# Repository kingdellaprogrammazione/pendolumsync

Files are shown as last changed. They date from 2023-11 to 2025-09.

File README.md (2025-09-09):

# Sincronizzazione di due pendoli accoppiati

In questa repository è presente il materiale prodotto per l'esame di Sistemi Complessi della triennale in fisica di Bologna. L'oggetto dello studio è il fenomeno di sincronizzazione tra due pendoli accoppiati tramite un'asta.
Di seguito è presentato un breve riassunto del lavoro effettuato; una descrizone completa è presente nel report.

## Analisi meccanica del moto di due pendoli accoppiati

<p align="center">
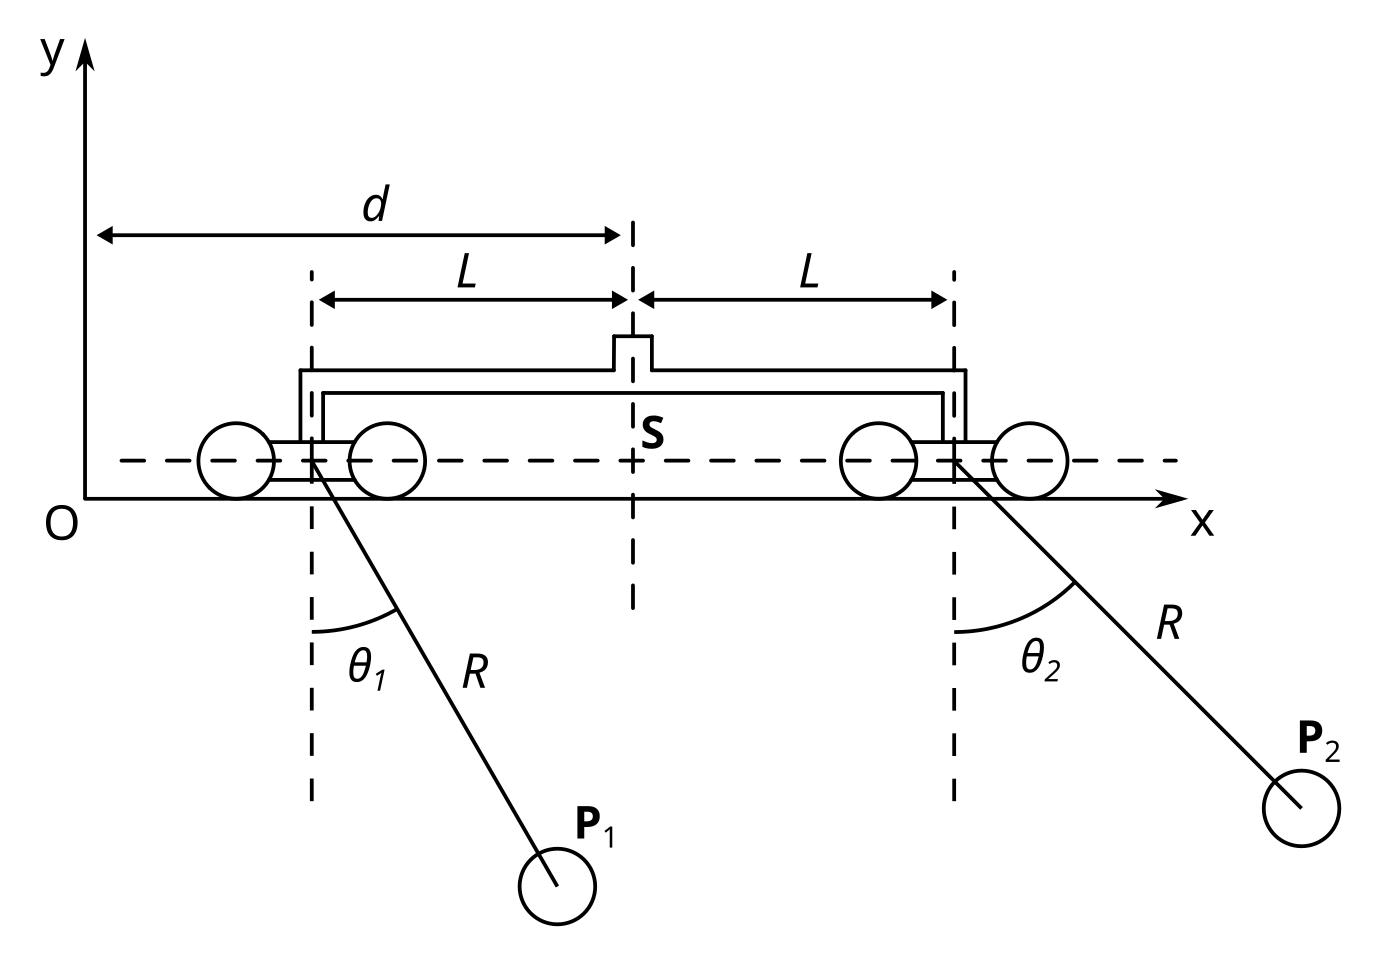
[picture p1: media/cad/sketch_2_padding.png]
  
</p>

Senza considerare attriti, dalla figura si calcola la lagrangiana del sistema, a meno di costanti, come

$$
\mathcal{L}_{PO} =  \left(m+ \frac{M}{2}\right) \dot{d}^2 + \frac{m R^2}{2}  (\dot\theta_1^2 + \dot\theta_2^2) + m \dot{d} R (\dot \theta_1 + \dot \theta_2) - \frac{m gR}{2} (\theta_1^2 + \theta_2^2) .
$$

## Equazioni del moto in assenza di attrito

Per proseguire è necessario approssimare la lagrangiana nel regime di piccole oscillazioni e sfruttare un cambio di coordinate per gli angoli: 

$$\begin{array}{c}
h = \theta_1 + \theta_2 , \\
q = \theta_1 - \theta_2.
\end{array}
$$

E' possibile utilizzare ora un'altra funzione, la funzione di Routh, per poter eliminare un grado di libertà. Si ottiene immediatamente

$$  \mathcal{R}_{PO} = \frac{1}{2} \frac{(p_d -mR\dot h)^2}{2m + M}- \frac{mR^2}{4}  (\dot{h}^2 + \dot{q}^2) + \frac{mgR}{4}(h^2 + q^2) . $$ 

Si può così completamente ricostruire il moto del sistema. Si nota che, partendo da una situazione iniziale arbitraria, la condizione di sincronizzazione in fase equivale alla richiesta che $q$ tenda a zero, mentre quella in controfase equivale alla richiesta che $h$ tenda a zero. Occorre fare attenzione al fatto
che però nella soluzione dell'equazione il moto evidentemente non può convergere, essendo hamiltoniano, ad una soluzione particolare, fatta eccezione per alcune condizioni iniziali patologiche.

## Equazioni del moto in presenza di attrito

Affinchè il moto converga ad una soluzione particolare, come accade nella realtà, è necessario tenere conto dei fenomeni dissipativi. Potrebbe ad esempio essere considerato l'attrito che si sviluppa nel perno dei pendoli, quello generato dal movimento delle ruote dei carrelli, sia radente che volvente, e quello tra l'aria e le varie componenti mobili. Si supponga di voler includere nelle equazioni del moto un termine proporzionale alle velocità angolari , con costante comune di proporzionalità gamma, avente le dimensioni di una frequenza. Riscrivendo le equazioni del moto e aggiugnendo alle forze generalizzate l'attrito citato sopra si ottengono due equazioni

$$  R \ddot \theta_i + \ddot d = - g \theta_i  - \gamma   \dot \theta_i, \qquad i =1,2 .
$$

Dopo qualche sostituzione, sfruttando la coordinata ciclica d si possono riscrivere le due equazioni con le nuove variabili.  La considerazione decisiva per osservare il fenomeno della sincronizzazione consiste nel considerare la costante gamma diversa per i due modi di oscillazione; differenziando le nuove costanti
con un pedice, si tiene conto di effetti dissipativi che influenzano in modo differente il modo di oscillazione in fase rispetto a quello in controfase.  È evidente quindi che se le costanti gamma sono diverse, l'ampiezza di uno di questi due modi va a zero più velocemente rispetto all'altro, sincronizzando il moto. In conclusione le equazioni considerate sono:

$$  
\begin{split}
  \ddot h + \gamma_h \dot h + \omega_h^2 h  = 0, \\
  \ddot q +\gamma_h \dot q + \omega_q^2 q = 0 .
  \end{split}
$$

# Apparato sperimentale

## Materiale utilizzato

Riferirsi al report.

## Realizzazione pratica del modello

Inizialmente la realizzazione del progetto era stata pensata tramite una rotaia a cuscino d'aria, per poter studiare il fenomeno, nella sua parte transiente, per un periodo di tempo lungo, grazie al poco attrito; questa idea però è stata abbandonata dopo alcuni tentativi per le numerose difficoltà sperimentali. Successivamente si è provato ad usare delle costruzioni giocattolo per la creazione di una rotaia e carrellini; purtroppo anche questo tentativo è stato accantonato a causa di notevoli imperfezioni e mancanza di allineamento tra i vari pezzi di rotaia.

In seguito si è pensato quindi di utilizzare un'altro tipo di rotaia di laboratorio, dotata di carrellini con ruote. La progettazione del modello si è rivolta, una volta recuperata l'apparecchiatura di laboratorio, alla costruzione dei supporti, disegnati tramite un software di modellizzazione tridimensionale e stampati con una stampante 3D. 

<p align="center">
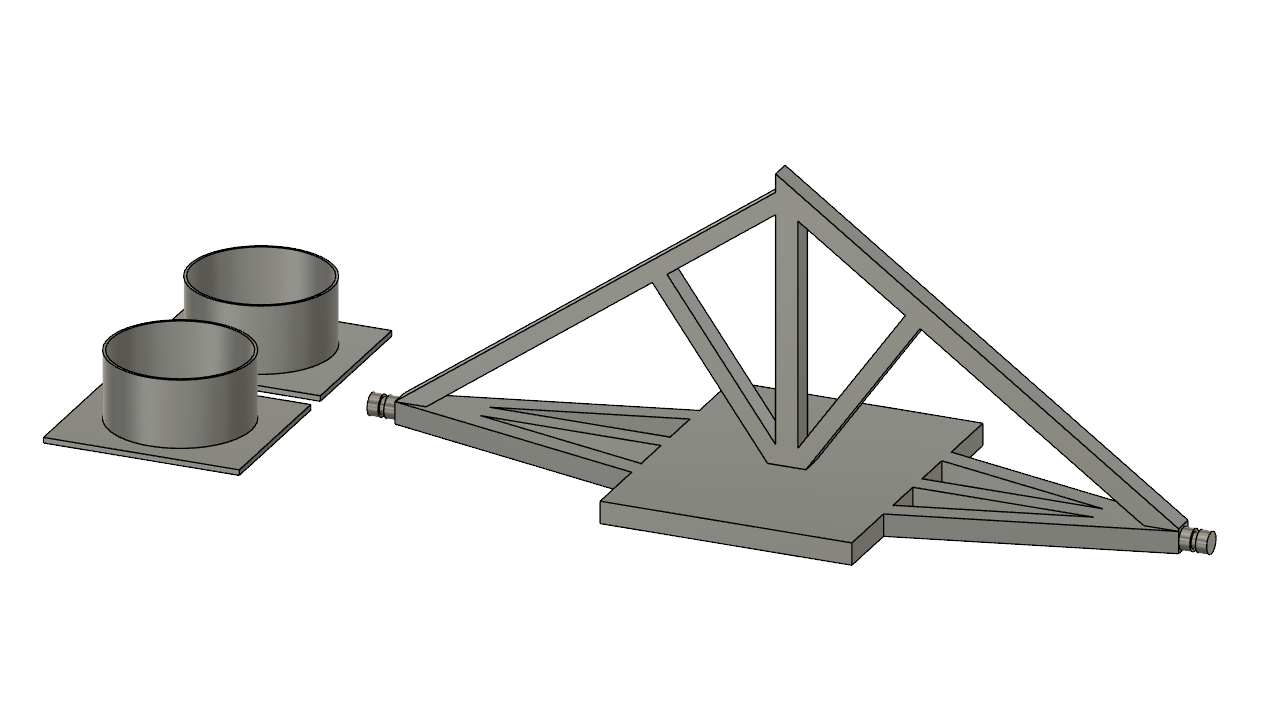
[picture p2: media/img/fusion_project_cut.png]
  
</p>

L'apparato sperimentale completo è mostrato nella figura seguente:

<p align="center">
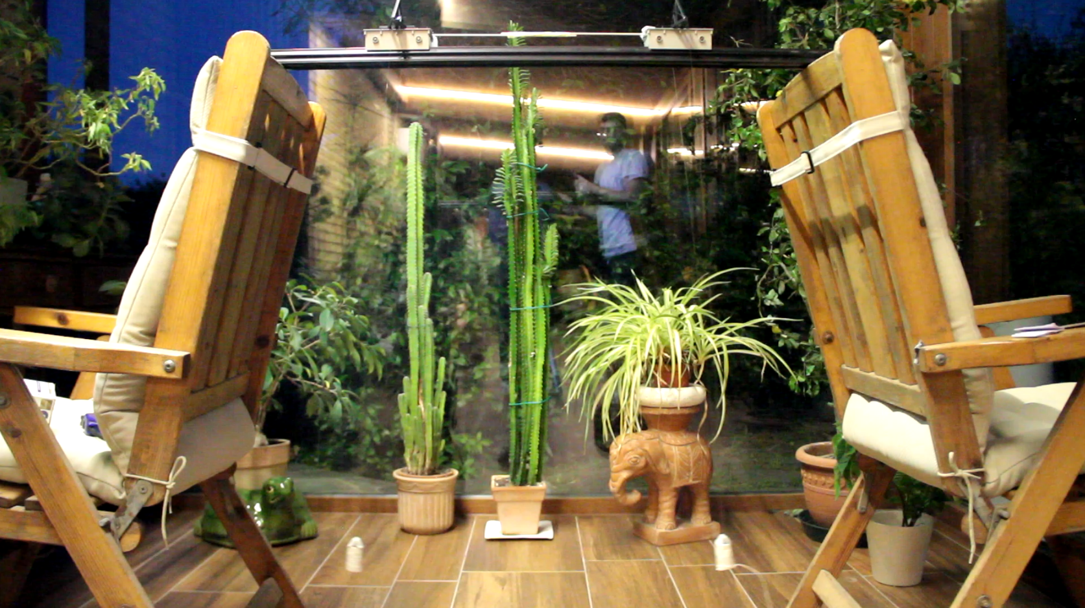
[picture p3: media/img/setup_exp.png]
  
</p>

## Esecuzione dell'esperimento

Una volta sistemati tutti gli elementi, sono stati acquisiti differenti video del fenomeno, avendo la cura di avere una condizione iniziale statica, con i tutti gli elementi fermi rispetto al sistema di riferimento della stanza. Questa ipotesi è stata  realizzata inizialmente collegando, dopo aver fermato il pendolo di sinistra, con un lungo spago fatto circolare attorno all'apparato, il pendolo e il carrello di destra. In questo modo si puntava ad eliminare l'errore dato dalla non coincidenza degli istanti di rilascio dei due elementi, che sarebbero invece stati messi in moto nello stesso momento al taglio dello spago. Questo sistema, però, è risultato inadatto in quanto lo spago, una volta tagliato, continuava a disturbare il movimento dell'apparecchio introducendo un nuovo attrito e distorcendo il fenomeno. Si è provato quindi ad agire nel modo più semplice: fermando il pendolo di sinistra, trattenendo con una mano il carrellino di destra e con l'altra lo spago collegato al rispettivo pendolo. 

## Scrittura dei programmi per l'acquisizione e l'elaborazione dati

Per quanto riguarda la scrittura dei programmi, si è scelto di utilizzare la libreria [OpenCV](https://opencv.org/), una libreria open source utilizzabile in particolare nel linguaggio di programmazione C++, destinata all'analisi di immagini e video. In questo esperimento la libreria è stata utilizzata nel per tracciare il movimento nel tempo dei pendoli e dei carrellini, in maniera automatizzata. E' stato utilizzato il C++ per la nota velocità in esecuzione rispetto a python. 

# Risultati e discussione

Il grafico degli angoli al trascorrere del tempo è mostrato nella figura seguente.

<p align="center">
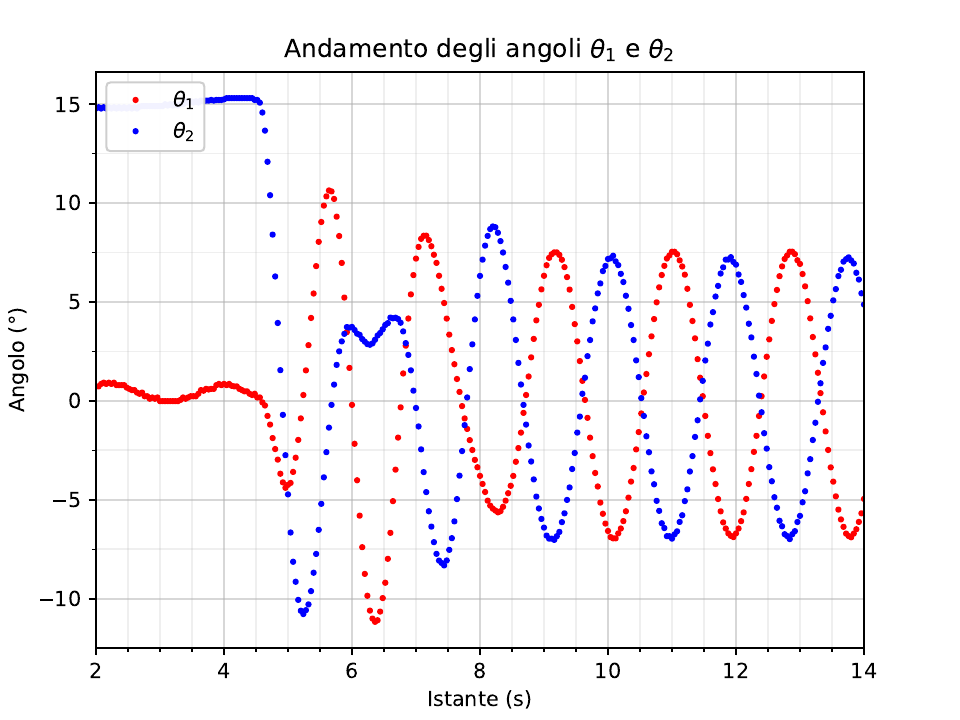
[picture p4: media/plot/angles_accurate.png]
  
</p>

Si nota come, dopo un breve periodo iniziale di quiete, in cui il pendolo 1 si trova in quiete, mentre il pendolo 2 descrive piccole oscillazioni dell'ampiezza di circa 1°, che si è cercato di ridurre il più possibile manualmente, il sistema viene lasciato libero di evolvere. Dopo un momento di transizione, in cui i pendoli e i carrellini descrivono il loro complicato moto, circa dall'istante 4.6 all'istante 8.5, il sistema mantiene il suo moto nella condizione di oscillazioni in controfase, quindi con i carrellini necessariamente fermi, per la conservazione della quantità di moto iniziale, nulla.

Possono quindi essere costruite e analizzate le variabili h e q mostrate al variare del tempo:

<p align="center">
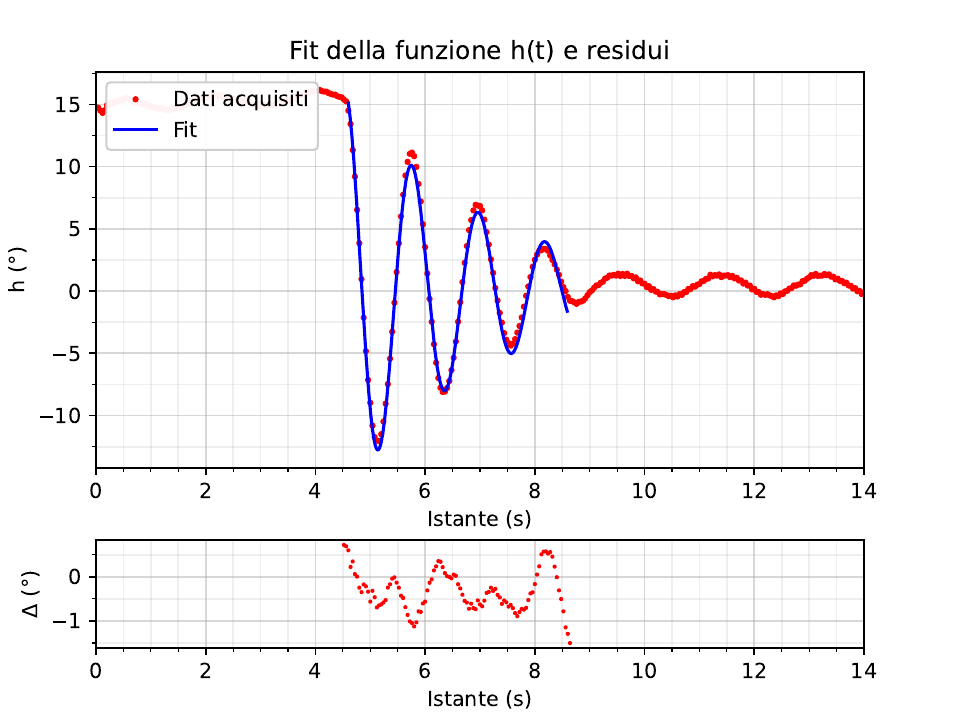
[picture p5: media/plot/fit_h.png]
  
</p>

<p align="center">
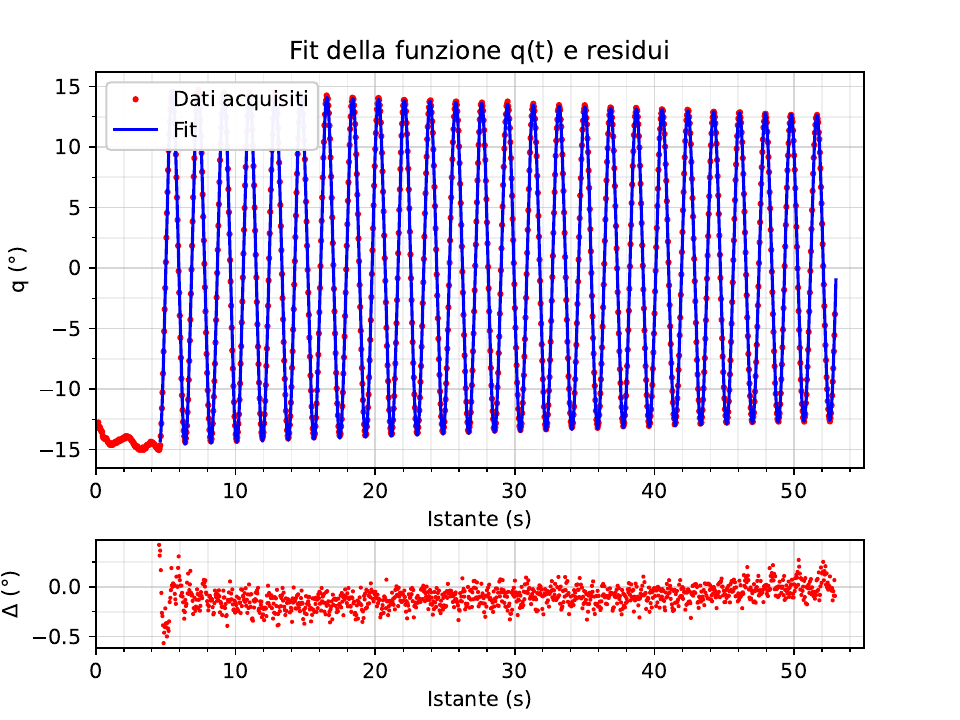
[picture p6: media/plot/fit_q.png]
  
</p>

In queste due figure sono anche presenti i due fit delle equazioni teoriche che dovrebbero regolare il moto delle due variabili; in basso sono mostrati anche i residui, ossia la differenza, calcolata punto per punto, tra i valori del fit e quelli dei punti acquisiti.

# Conclusioni

In conclusione, è stata osservata con successo la sincronizzazione di due pendoli, ossia la diminuzione dell'ampiezza a zero di un modo normale di oscillazione del sistema, fatto dovuto a differenti tassi di dissipazione di energia nei due modi appena citati. I due coefficienti $\gamma$ sono stati stimati essere pari rispettivamente a 0.77 ± 0.02 Hz per il modo in fase e 0.00631 ± 0.00006 Hz per quello in controfase.
Notiamo infine che la stima dei coefficienti di attrito data dal fit è in accordo con l'idea intuitiva legata alla caratteristica del modo di oscillazione in cui il carrello è fermo, ossia alla minor dissipazione di energia rispetto a quello in cui il carrello oscilla in opposizione di fase rispetto ai pendoli; ciò è dovuto soprattutto al maggiore attrito generato durante lo scorrimento sulla rotaia che si somma al normale attrito generato sul perno dalle oscillazioni dei pendoli. Questa sorgente di attrito è circa di 2 ordini di grandezza superiore rispetto all'altra.

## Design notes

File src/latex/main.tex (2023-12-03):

\documentclass[11pt, a4paper, twoside, italian]{article}

\usepackage{blindtext}
\usepackage{geometry}
\usepackage{setspace}
\usepackage{titlesec}
\usepackage{indentfirst}
\usepackage{graphicx}
\usepackage{babel}
\usepackage{multicol}
\usepackage{amsmath}
\usepackage{subcaption}
\usepackage[hang, flushmargin, multiple, bottom]{footmisc}
\usepackage{float}
\usepackage{array}
\usepackage{booktabs}
\usepackage{url}
\usepackage{csvsimple}
\usepackage{colortbl}
\usepackage{multicol}
\usepackage{enumerate}
\usepackage{multirow}
\usepackage{booktabs}
\usepackage{siunitx}
\usepackage{subcaption}
\usepackage[margin=0.2cm]{caption}
\usepackage{longtable}
\usepackage{physics}
\usepackage{comment}
\usepackage{listings}
\usepackage{xcolor}
\usepackage{enumitem}
\usepackage{wrapfig}
\usepackage{hyperref}
\usepackage{cleveref}
\usepackage[ddmmyyyy]{datetime}
\usepackage[export]{adjustbox}
% for watermark
%\usepackage{draftwatermark}
%\SetWatermarkText{\includegraphics{../../media/img/draft_watermark.png}}

\titlespacing*{\section}{0px}{3mm}{1mm}
\titlespacing*{\subsection}{0px}{3mm}{1mm}
\geometry{
  left=2cm,
  right=2cm,
  top=2cm,
  bottom=2cm
}
\setlength{\parindent}{10mm}

\author{Edoardo Frulla}
\date{Corso "Introduzione ai sistemi complessi" \\ \vspace{0.3cm} I semestre a.a. 2022/2023 \\ \vspace{0.3cm} \today}
\title{Sincronizzazione di due pendoli accoppiati}  

\definecolor{codegreen}{rgb}{0,0.6,0}
\definecolor{codegray}{rgb}{0.5,0.5,0.5}
\definecolor{codepurple}{rgb}{0.58,0,0.82}
\definecolor{backcolour}{rgb}{0.95,0.95,0.92}
  
\lstdefinestyle{mystyle}{
  backgroundcolor=\color{backcolour},   
  commentstyle=\color{codegreen},
  keywordstyle=\color{magenta},
  numberstyle=\tiny\color{codegray},
  stringstyle=\color{codepurple},
  basicstyle=\ttfamily\footnotesize,
  breakatwhitespace=false,         
  breaklines=true,                 
  captionpos=b,                    
  keepspaces=true,                 
  numbers=left,                    
  numbersep=5pt,                  
  showspaces=false,                
  showstringspaces=false,
  showtabs=false,               
  tabsize=2,
  inputencoding = utf8,  % Input encoding
  extendedchars = true,  % Extended ASCII
  literate      =        % Support additional characters
    {á}{{\'a}}1  {é}{{\'e}}1  {í}{{\'i}}1 {ó}{{\'o}}1  {ú}{{\'u}}1
    {Á}{{\'A}}1  {É}{{\'E}}1  {Í}{{\'I}}1 {Ó}{{\'O}}1  {Ú}{{\'U}}1
    {à}{{\`a}}1  {è}{{\`e}}1  {ì}{{\`i}}1 {ò}{{\`o}}1  {ù}{{\`u}}1
    {À}{{\`A}}1  {È}{{\`E}}1  {Ì}{{\`I}}1 {Ò}{{\`O}}1  {Ù}{{\`U}}1
    {ä}{{\"a}}1  {ë}{{\"e}}1  {ï}{{\"i}}1 {ö}{{\"o}}1  {ü}{{\"u}}1
    {Ä}{{\"A}}1  {Ë}{{\"E}}1  {Ï}{{\"I}}1 {Ö}{{\"O}}1  {Ü}{{\"U}}1
    {â}{{\^a}}1  {ê}{{\^e}}1  {î}{{\^i}}1 {ô}{{\^o}}1  {û}{{\^u}}1
    {Â}{{\^A}}1  {Ê}{{\^E}}1  {Î}{{\^I}}1 {Ô}{{\^O}}1  {Û}{{\^U}}1
    {œ}{{\oe}}1  {Œ}{{\OE}}1  {æ}{{\ae}}1 {Æ}{{\AE}}1  {ß}{{\ss}}1
    {ẞ}{{\SS}}1  {ç}{{\c{c}}}1 {Ç}{{\c{C}}}1 {ø}{{\o}}1  {Ø}{{\O}}1
    {å}{{\aa}}1  {Å}{{\AA}}1  {ã}{{\~a}}1  {õ}{{\~o}}1 {Ã}{{\~A}}1
    {Õ}{{\~O}}1  {ñ}{{\~n}}1  {Ñ}{{\~N}}1  {¿}{{?`}}1  {¡}{{!`}}1
    {°}{{\textdegree}}1 {º}{{\textordmasculine}}1 {ª}{{\textordfeminine}}1
    {£}{{\pounds}}1  {©}{{\copyright}}1  {®}{{\textregistered}}1
    {«}{{\guillemotleft}}1  {»}{{\guillemotright}}1  {Ð}{{\DH}}1  {ð}{{\dh}}1
    {Ý}{{\'Y}}1    {ý}{{\'y}}1    {Þ}{{\TH}}1    {þ}{{\th}}1    {Ă}{{\u{A}}}1
    {ă}{{\u{a}}}1  {Ą}{{\k{A}}}1  {ą}{{\k{a}}}1  {Ć}{{\'C}}1    {ć}{{\'c}}1
    {Č}{{\v{C}}}1  {č}{{\v{c}}}1  {Ď}{{\v{D}}}1  {ď}{{\v{d}}}1  {Đ}{{\DJ}}1
    {đ}{{\dj}}1    {Ė}{{\.{E}}}1  {ė}{{\.{e}}}1  {Ę}{{\k{E}}}1  {ę}{{\k{e}}}1
    {Ě}{{\v{E}}}1  {ě}{{\v{e}}}1  {Ğ}{{\u{G}}}1  {ğ}{{\u{g}}}1  {Ĩ}{{\~I}}1
    {ĩ}{{\~\i}}1   {Į}{{\k{I}}}1  {į}{{\k{i}}}1  {İ}{{\.{I}}}1  {ı}{{\i}}1
    {Ĺ}{{\'L}}1    {ĺ}{{\'l}}1    {Ľ}{{\v{L}}}1  {ľ}{{\v{l}}}1  {Ł}{{\L{}}}1
    {ł}{{\l{}}}1   {Ń}{{\'N}}1    {ń}{{\'n}}1    {Ň}{{\v{N}}}1  {ň}{{\v{n}}}1
    {Ő}{{\H{O}}}1  {ő}{{\H{o}}}1  {Ŕ}{{\'{R}}}1  {ŕ}{{\'{r}}}1  {Ř}{{\v{R}}}1
    {ř}{{\v{r}}}1  {Ś}{{\'S}}1    {ś}{{\'s}}1    {Ş}{{\c{S}}}1  {ş}{{\c{s}}}1
    {Š}{{\v{S}}}1  {š}{{\v{s}}}1  {Ť}{{\v{T}}}1  {ť}{{\v{t}}}1  {Ũ}{{\~U}}1
    {ũ}{{\~u}}1    {Ū}{{\={U}}}1  {ū}{{\={u}}}1  {Ů}{{\r{U}}}1  {ů}{{\r{u}}}1
    {Ű}{{\H{U}}}1  {ű}{{\H{u}}}1  {Ų}{{\k{U}}}1  {ų}{{\k{u}}}1  {Ź}{{\'Z}}1
    {ź}{{\'z}}1    {Ż}{{\.Z}}1    {ż}{{\.z}}1    {Ž}{{\v{Z}}}1
    % ¿ and ¡ are not correctly displayed if inconsolata font is used
    % together with the lstlisting environment. Consider typing code in
    % external files and using \lstinputlisting to display them instead.      
    % reference to this answer https://tex.stackexchange.com/questions/24528/having-problems-with-listings-and-utf-8-can-it-be-fixed
    % and https://tex.stackexchange.com/questions/105672/special-characters-in-input-file
}

\lstset{style=mystyle}

\sisetup{separate-uncertainty=true}
%per mettere il più meno

\begin{document}
\maketitle
    \begin{abstract}
        In questo documento si introduce il fenomeno emergente della sincronizzazione.
        Si sceglie poi un sistema composto da due pendoli accoppiati per analizzare le caratteristiche
        dinamiche che lo portano alla sincronizzazione, giungendo alla conlcusione che
        la causa del fenomeno sia la differenza tra i tassi di dissipazione dei principali
        modi normali di oscillazione.
        Infine si effettua un esperimento per valutare la bontà della previsione teorica.
    \end{abstract}

\section{Introduzione}
La sincronizzazione è un particolare fenomeno che si manifesta in natura in differenti modalità: ne sono esempi gli sciami di lucciole che tendono a lampeggiare all'unisono, le cellule del cuore umano che emettono impulsi elettrici in fase permettendo le contrazioni cardiache, gli applausi che si sviluppano nel pubblico durante le opere teatrali e i neuroni che emettono segnali elettrici, amplificandone gli effetti, durante gli episodi di epilessia.
In tutti questi casi sono considerate situazioni in cui i singoli elementi che causano il fenomeno, a cui è associata una grandezza caratteristica che oscilla secondo un periodo proprio generalmente arbitrario, si trovano ad interagire e influenzandosi l'un l'altro giungono in qualche modo alla sincronizzazione più o meno completa dell'insieme di cui fanno parte.
Le interazioni che abbiamo descritto fino ad ora sono però manifestazione di interazioni non fondamentali dal punto di vista fisico: si tratta di fenomeni emergenti. 
Esistono però anche delle situazioni in cui la sincronizzazione è attribuibile alle interazioni fisiche fondamentali: possiamo per esempio pensare ai sistemi meccanici composti da pendoli o metronomi accoppiati.

Un problema di questo tipo fu affrontato per la prima volta nel Febbraio 1665, dal fisico Olandese Christiaan Huygens: doveva affrontare il problema di migliorare la precisione degli orologi a pendolo, anche essi da lui inventati. Si trovava nella sua stanza a causa di una "leggera indisposizione" quando si accorse che due orologi a pendolo che aveva costruito si erano spontaneamente sincronizzati. Provò allora, sospettando un accoppiamento dovuto al mezzo con cui si trovavano entrambi in contatto, a svolgere alcuni esperimenti, in particolare agganciandone due a un supporto in legno sospeso tra due sedie, come si nota da \cref{pendoli_huygens}.
\begin{figure}
    \centering
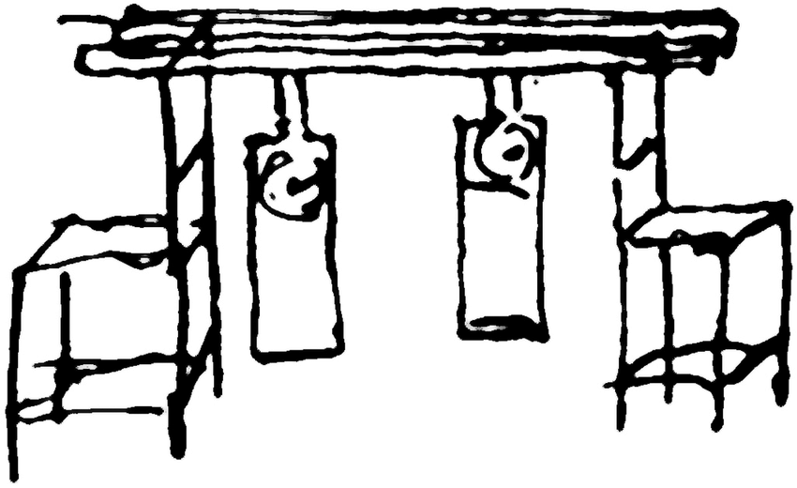
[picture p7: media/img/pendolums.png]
    
    \caption{\textit{Schema della situazione sperimentale disegnato da Huygens. I due orologi sono sospesi a un supporto comune.}}
    \label{pendoli_huygens}
\end{figure}
Un problema più semplice da affrontare rispetto a quello dei due orologi a pendolo è quello di due pendoli posti su una base comune, libera di muoversi lungo un asse.
\section{Analisi meccanica del moto di due pendoli accoppiati}
\begin{figure}[h]
    \centering
    
    \caption{\textit{Modello del sistema costruito con indicate
     le grandezze rilevanti. Le lettere maiuscole in grassetto indicano dei punti, quelle in corsivo delle 
     costanti; le minuscole invece indicano le variabili.} }
    \label{pendolicorpolibero}
\end{figure}
Innanzitutto si consideri il diagramma indicato in \cref{pendolicorpolibero}.
I tre corpi coinvolti nella dinamica sono i due pendoli, il cui centro 
geometrico è indicato dai punti $\mathbf{P}_1$ e $\mathbf{P}_2$, entrambi di massa $m$,
e il supporto rigido, costituito da due carrellini identici collegati tra loro da un'asta,
indicato dal punto $\mathbf{S}$, arbitrariamente fissato lungo l'asse di simmetria del sistema 
parallelo all'asse $y$, di massa $M$. In questo caso, per comodità il punto $\mathbf{S}$ 
viene fissato lungo l'asse nel punto di intersezione con l'asse di simmetria dei carrellini
parallelo all'asse $x$.

Si assuma che il sistema sia libero di muoversi esclusivamente in un piano fissato, in questo caso
il piano $xy$, e che il moto del supporto sia ristretto alla direzione $x$ (è "appoggiato" sull'asse $x$).
Si supponga che le masse dell'asta e dei fili colleganti i carrellini tra loro
e con le masse oscillanti $\mathbf{P}$ siano trascurabili rispetto alle restanti; 
inoltre si trascurino anche le masse delle ruote dei carrellini, che, se presenti, si assume ruotino senza strisciare.
Per quanto riguarda le masse dei pendoli puntiformi, queste sono pensate fissate nel centro geometrico degli stessi.
In questo modo è possibile ottenere una notevole semplificazione della trattazione analitica,
descrivendo comunque con una buona approssimazione il moto degli elementi principali.

È possibile quindi ricavare le coordinate dei tre elementi rilevanti, ossia i due pendoli e il supporto:
\begin{gather*}
\mathbf{P}_1 = (d - L + R \sin \theta_1, S_y - R \cos \theta_1 ) \, , \\
\mathbf{P}_2 = (d + L + R \sin \theta_2, S_y - R \cos \theta_2 ) \, , \\
\mathbf{S} = (d , S_y) \, .
\end{gather*}
Calcolando quindi l'energia cinetica per ogni oggetto:
\begin{gather*}
K_{\mathbf{P}_1}=  \frac{m}{2} \lVert \dot{\mathbf{P}}_1 \rVert^2 =  \frac{m}{2}(\dot{d}^2 + R^2 \dot\theta_1^2+ 2\dot{d}R\cos\theta_1 \dot{\theta_1}) \, , \\
K_{\mathbf{P}_2} = \frac{m}{2} \lVert \dot{\mathbf{P}}_2 \rVert^2 =  \frac{m}{2}(\dot{d}^2 + R^2 \dot\theta_2^2+ 2\dot{d}R\cos\theta_2 \dot{\theta_2}) \, , \\
K_{\mathbf{S}} =  \frac{M}{2} \lVert \dot{\mathbf{S}} \rVert^2 = \frac{M}{2} \dot{d}^2 \, .
\end{gather*}
L'energia potenziale invece è:
\begin{gather*}
V_{\mathbf{P}_1}= mg P_{1y} = mg (S_y - R \cos \theta_1 ) \, , \\
V_{\mathbf{P}_2} = mg P_{2y} = mg (S_y - R \cos \theta_2 ) \, , \\
V_{\mathbf{S}} = mg S_{y} \, .
\end{gather*}
E quindi la lagrangiana del sistema si calcola, a meno di costanti, come
\begin{equation*}
\mathcal{L} = K_{TOT} - V_{TOT} = \left(m+ \frac{M}{2}\right) \dot{d}^2 + \frac{m R^2}{2}  (\dot\theta_1^2 + \dot\theta_2^2) + m \dot{d} R (\cos\theta_1 \dot\theta_1 + \cos \theta_2 \dot \theta_2) + mgR(\cos\theta_1 + \cos \theta_2) \, .
\end{equation*}
\subsection{Equazioni del moto in assenza di attrito}
Per proseguire è necessario approssimare
la lagrangiana nel regime di piccole oscillazioni:
\begin{equation}
\mathcal{L}_{PO} =  \left(m+ \frac{M}{2}\right) \dot{d}^2 + \frac{m R^2}{2}  (\dot\theta_1^2 + \dot\theta_2^2) + m \dot{d} R (\dot \theta_1 + \dot \theta_2) - \frac{m gR}{2} (\theta_1^2 + \theta_2^2) \, .
\label{lagrangianapo}
\end{equation}
Si nota immediatamente che nella lagrangiana è presente una coordinata ciclica, $d$; c'è
 quindi un integrale primo del moto, cioè una quantità che resta costante durante 
l'evoluzione temporale del sistema:
\begin{equation}
p_d = \frac{\partial \mathcal{L}_{PO}}{\partial \dot{d}} =(2m+M) \dot d + m R (\dot\theta_1 + \dot \theta_2) \, .
\label{ciclica}
\end{equation}
Si può sfruttare adesso un conveniente cambio di coordinate per gli angoli:
\begin{equation}
\setlength\arraycolsep{0pt}
\renewcommand\arraystretch{1.25}
\left\{
\begin{array}{c}
h = \theta_1 + \theta_2  \\
q = \theta_1 - \theta_2
\end{array}
\right.
,
\label{definizionehq}
\end{equation}
notando che
\begin{equation*}
  \theta_1^2 + \theta_2^2 = \frac{h^2 +q^2}{2} \, .
\end{equation*}
Le relazioni precedenti valgono anche tra le derivate.
Riscrivendo la lagrangiana si ottiene
\begin{equation*}
\mathcal{L}_{PO} =  \left(m+ \frac{M}{2}\right) \dot{d}^2 + \frac{mR^2}{4}  (\dot{h}^2 + \dot{q}^2) + m  R \dot{d}\dot{h} - \frac{mgR}{4}(h^2 + q^2) \, .
\end{equation*}
L'\cref{ciclica} inoltre diventa 
\begin{equation*}
  p_d = \frac{\partial \mathcal{L}_{PO}}{\partial \dot{d}} =(2m+M) \dot d + m R \dot h \, .
\end{equation*}
E' possibile utilizzare ora un'altra funzione, la funzione di Routh $\mathcal{R}_{PO}$, per poter eliminare 
un grado di libertà nelle equazioni del moto. Questa viene ricavata a partire dalla lagrangiana, introducendo solamente il
momento $p_d$:
\begin{equation*}
\mathcal{R}_{PO}(h,\dot h, q, \dot q, d, p_d )  = 
p_d \dot{d}(d, p_d, h,\dot h, q, \dot q)- \mathcal{L}_{PO}(h,\dot h, q, \dot q, d, \dot{d}(d, p_d, h,\dot h, q, \dot q)) \, ,
\end{equation*}
dove sono state esplicitate le dipendenze dalle variabili. 
In particolare si nota che nella lagrangiana bisogna scrivere $\dot d$ sfruttando l'\cref{ciclica}.
Si ottiene immediatamente 
\begin{equation*}
  \mathcal{R}_{PO} = \frac{1}{2} \frac{(p_d -mR\dot h)^2}{2m + M}- \frac{mR^2}{4}  (\dot{h}^2 + \dot{q}^2) + \frac{mgR}{4}(h^2 + q^2) \, .
\end{equation*}
Da questa equazione si possono ricavare le equazioni del moto, le più importanti sono 
\begin{equation}
  \dot p_d = 0 \, ,
  \label{conservazione}
\end{equation}
che è ovviamente coerente con la conservazione di $p_d$ notata in \cref{ciclica}, e
\begin{equation}
  \begin{split}
  \ddot h = -\frac{\alpha}{R} h \, ,\\
  \ddot q = - \frac{g}{R} q \, ,
  \end{split}
  \label{equazionifinalinondissipate}
\end{equation}
utilizzando l'\cref{conservazione} e ponendo $\alpha = \frac{(2m + M) g}{M} $.
Con queste equazioni a disposizione si può completamente ricostruire il moto del sistema.
Si nota che, partendo da una situazione iniziale arbitraria,
la condizione di sincronizzazione in fase equivale alla richiesta che $q$ tenda a zero, mentre quella in controfase
equivale alla richiesta che $h$ tenda a zero. 
Occorre fare attenzione al fatto che però nella soluzione in \cref{equazionifinalinondissipate} sia $h$ che $q$ descrivono moti oscillatori con frequenza rispettiva
$\omega_h = \sqrt{\frac{\alpha}{R} \vphantom{\frac{g}{R}}}$ e $\omega_q = \sqrt[]{\frac{g}{R}}$.
Le uniche soluzioni per cui i pendoli oscillano sincronizzati sono quelle per cui una tra $h$ o $q$ è nulla
all'inizio del moto, restando quindi nulla per tutti gli istanti successivi.
Il moto evidentemente non converge ad una soluzione particolare, attraversa invece entrambe le configurazioni di sincronizzazione 
permanendo per il resto degli istanti in una combinazione delle due soluzioni.
\label{sezionesenzaattrito}

\subsection{Equazioni del moto in presenza di attrito}
\label{sezioneattrito}
Affinchè il moto converga ad una soluzione particolare, come accade nella realtà, 
è necessario tenere conto dei fenomeni dissipativi.
Potrebbe ad esempio essere considerato l'attrito che si sviluppa nel perno 
dei pendoli, quello generato dal movimento delle ruote dei
 carrelli, sia radente che volvente, e quello tra l'aria e le varie 
 componenti mobili.
Si supponga di voler includere nelle equazioni del moto un termine 
proporzionale alle velocità angolari $\dot \theta_1$ e $\dot \theta_2$, con costante comune di 
proporzionalità $\gamma$, avente le dimensioni di una frequenza. 
Riscrivendo le equazioni del moto 
per queste due variabili, ricavandole dalla lagrangiana in \cref{lagrangianapo} e semplificando i fattori in comune
si ottiene
\begin{equation*}
    R \ddot \theta_i + \ddot d = - g  \theta_i , \qquad i =1,2 
\end{equation*}
e si nota che è possibile aggiungere al secondo membro, in cui sono scritte le 
forze generalizzate, l'attrito citato sopra, agente ovviamente in verso 
opposto alla velocità:
\begin{equation*}
  R \ddot \theta_i + \ddot d = - g \theta_i  - \gamma   \dot \theta_i, \qquad i =1,2 \, .
\end{equation*}
Sostituendo la derivata dell'\cref{ciclica}
\begin{equation*}
  (2m + M) \ddot d = -mR (\ddot \theta_1 + \ddot \theta_2) 
\end{equation*} 
nell'equazione precedente si giunge alla coppia di equazioni:
\begin{equation*}
  R \ddot \theta_i -\frac{m}{2m + M}R (\ddot \theta_1 + \ddot \theta_2) 
  = - g \theta_i  - \gamma   \dot \theta_i \, , \qquad i =1,2 \, ,
\end{equation*}
che dopo qualche passaggio algebrico si possono riscrivere con le variabili
$h$ e $q$:
\begin{equation*}
  \begin{split}
  (R- \frac{2m}{2m + M}R) \ddot h + \gamma \dot h + g h  = 0 \, , \\
  R \ddot q +\gamma \dot q + g q = 0 \, .
  \end{split}
\end{equation*}
Manipolando algebricamente questa equazione, ridefinendo la costante
$\gamma$ e utilizzando le frequenze definite in precedenza si giunge infine a
\begin{equation*}
  \begin{split}
  \ddot h + \gamma \dot h + \omega_h^2 h  = 0 \, ,\\
  \ddot q +\gamma \dot q + \omega_q^2 q = 0 \, .
  \end{split}
\end{equation*}
La considerazione decisiva per osservare il fenomeno della sincronizzazione 
consiste nel considerare la costante $\gamma$ diversa per i due modi di oscillazione;
differenziando le nuove costanti con un pedice, si tiene conto di 
effetti dissipativi che influenzano in modo differente il modo di oscillazione
in fase rispetto a quello in controfase.
Le soluzioni generali di queste equazioni sono del tipo:
\begin{align}
    h(t) &= A_h e^{- \frac{\gamma_h}{2} t} \cos(\tilde{\omega}_h t + \beta_h) \label{equazionefinaleh} \, , \\
    q(t) &= A_q e^{- \frac{\gamma_q}{2} t} \cos(\tilde{\omega}_q t + \beta_q) \label{equazionefinaleq} \, ,
\end{align}
con $A_h$, $A_q$, $\beta_h$ e $\beta_q$ costanti reali, e dove 
\begin{equation}
\tilde{\omega}_i = \sqrt{\omega_i^2 -\left( \frac{\gamma_i}{2} \right)^2} \qquad 
i = h,q 
\, .
\label{equation:omegadef}
\end{equation}
È evidente quindi che se le costanti $\gamma$ sono diverse, l'ampiezza di uno di questi due modi va a zero più velocemente rispetto 
all'altro, sincronizzando il moto.

\section{Apparato sperimentale}
\subsection{Materiale utilizzato}

Durante l'esperimento sono stati coinvolti diversi elementi, tra cui:
\begin{enumerate}
      \item rotaia e carrellini\footnote{Attrezzatura gentilmente concessa dal liceo E.Medi di Senigallia}, mostrati in \cref{photo_crane}, con basso coefficiente di attrito solitamente
      utilizzati in esperimenti relativi alla conservazione della quantità
      di moto;
      \item due alte sedie in legno;
      \item filo di nylon trasparente;
      \item due strutture identiche, mostrate in \cref{photo_crane}, progettate autonomamente e stampate in 3D;
      \item scotch di carta;
      \item monete varie;
      \item spago da cucina;
      \item supporti in legno per spiedini.
\end{enumerate}
\begin{figure}[h!]
  \centering
\begin{minipage}[t]{0.45\textwidth}
  \centering
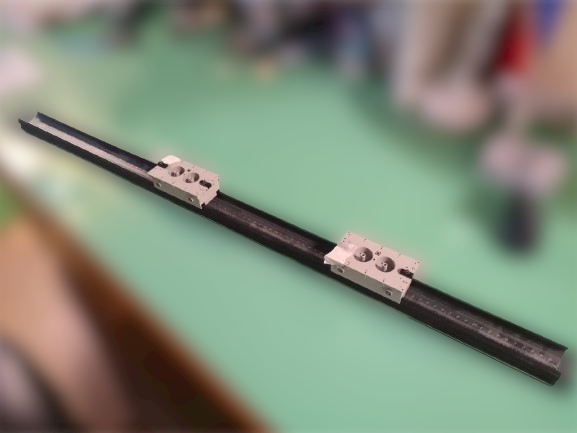
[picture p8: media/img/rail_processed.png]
  
  \caption{\textit{La rotaia e i carrellini presi in prestito.}}
  \label{photo_rail}
\end{minipage}
\begin{minipage}[t]{0.45\textwidth}
  \centering
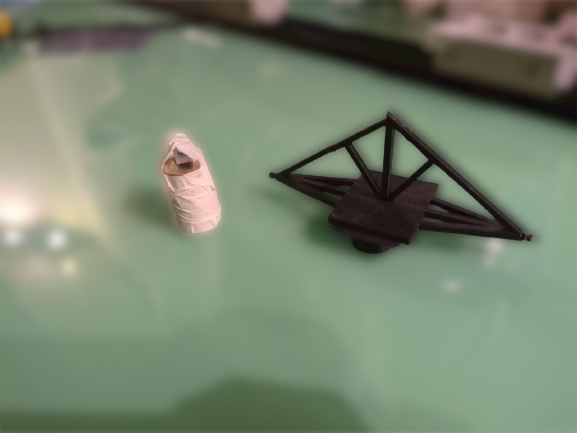
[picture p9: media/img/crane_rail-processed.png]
  
  \caption{\textit{Il pendolo (sinistra) e la struttura stampata in 3D dopo l'assemblaggio
  (destra).}}
  \label{photo_crane}
\end{minipage}
\end{figure}

\subsection{Strumenti di misura}

Per quanto riguarda gli strumenti di misura, sono stati invece utilizzati:
\begin{enumerate}
  \item bilancia da cucina (risoluzione \SI{1}{\g});
  \item macchina fotografica semi-professionale;
  \item treppiede per macchina fotografica;
  \item metro estendibile (risoluzione \SI{1}{\milli\m});
  \item livella a bolla;
  \item libreria di object tracking della suite OpenCV\footnote{https://opencv.org/}.
\end{enumerate}
\subsection{Realizzazione pratica del modello}
Inizialmente la realizzazione del progetto era stata pensata tramite 
una rotaia a cuscino d'aria, per poter studiare il fenomeno, nella sua parte transiente, 
per un periodo di tempo lungo, grazie al poco attrito; questa idea però è stata abbandonata dopo alcuni tentativi per
le numerose difficoltà sperimentali. In \cref{photo_crane_air} è mostrato uno dei modelli di supporto
progettati e stampati in 3D montabili sui carrellini della rotaia.
In seguito si è provato ad usare delle costruzioni giocattolo per la creazione di una rotaia
e carrellini; purtroppo anche questo tentativo è stato accantonato a causa di 
notevoli imperfezioni e mancanza di allineamento tra i vari pezzi di rotaia. 
Un esempio di una parte della costruzione è mostrato in \cref{photo_lego}.

\begin{figure}[h!]
  \centering
\begin{minipage}{0.45\textwidth}
  \centering
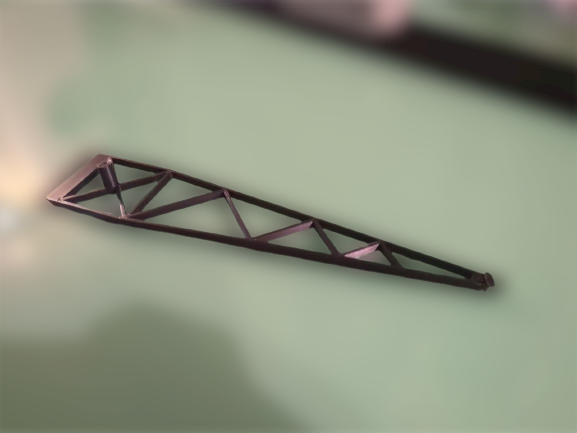
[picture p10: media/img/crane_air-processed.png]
  
  \caption{\textit{Parte della struttura relativa alla rotaia a cuscino d'aria.}}
  \label{photo_crane_air}
\end{minipage}
\begin{minipage}{0.45\textwidth}
  \centering
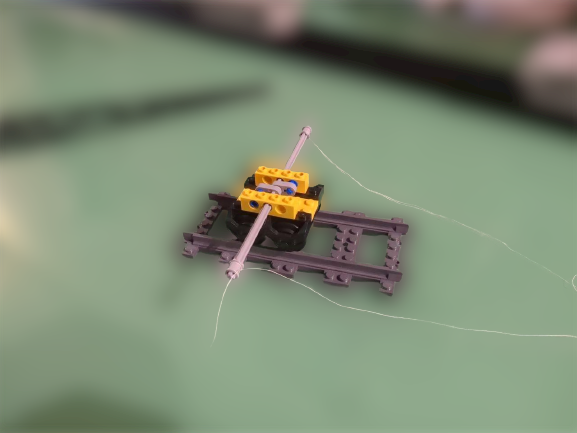
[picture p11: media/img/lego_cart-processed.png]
  
  \caption{\textit{Il modellino realizzato a partire da costruzioni giocattolo.}}
  \label{photo_lego}
\end{minipage}
\end{figure}

In seguito si è pensato quindi di utilizzare un'altro tipo di rotaia di laboratorio, dotata
di carrellini con ruote.
La progettazione del modello si è rivolta, una volta recuperata l'apparecchiatura
di laboratorio, alla costruzione dei supporti, disegnati tramite un
software di modellizzazione tridimensionale e stampati con una stampante 3D.
Una volta stampati diversi prototipi e scelto quello migliore sono state incollate
tra loro le due parti costituenti il pezzo finale indicato in \cref{photo_crane}, i cui modelli sono mostrati
in \cref{photo_piece}, e, 
incastrato il pezzo sopra ciascun carrellino, si è costruito il supporto tramite due alte sedie
sopra le quali è stata posta la rotaia. 
\begin{figure}[h!]
  \centering
  
  \caption{\textit{Le parti della struttura mostrata in \cref{photo_crane}, visualizzate nel programma
  di modellazione 3D.}}
  \label{photo_piece}
\end{figure}
È fondamentale sottolineare come si siano scelte le sedie più alte disponibili,
in quanto la lunghezza del pendolo doveva essere grande
per permettere poi l'uso dell'approssimazione di piccole oscillazioni,
non impedendo la chiara manifestazione del fenomeno della sincronizzazione.
I carrellini sono poi stati collegati tra loro tramite due bastoncini 
di legno solitamente utilizzati per la cottura degli spiedini.
La massa complessiva dei due carrellini, considerando il connettore trascurabile, è risultata essere pari a 
\SI{160 \pm 1}{\g}.
È stato controllato che lo sfondo presente dietro le
due sedie fosse inoltre fisso, ossia privo di oggetti
in movimento, per favorire il processo di tracking.
A questo punto sono stati costruiti i due pendoli identici, tramite svariate 
monete raggruppate saldamente insieme grazie all'uso dello scotch di carta, 
pesanti ciascuno \SI{139 \pm 1}{\g}.
Le monete sono state scelte per la loro elevata densità e modularità: è 
stato possibile infatti costruire diversi pendoli, di dimensioni pressochè
uguali ma di masse sensibilmente diverse gli uni dagli altri.
Sono quindi stati tagliati due pezzi approssimativamente
uguali di filo di nylon, lunghi abbastanza da sfruttare l'intera altezza 
fornita dalle due sedie, e sono poi stati agganciati ai pendoli tramite un pezzo di una nota 
marca di costruzioni giocattolo. Questi due tratti di filo sono stati poi regolati,
con l'ausilio del metro,
tramite la realizzazione di un numero adeguato di avvolgimenti nel perno di 
aggancio, fino ad ottenere una lunghezza del pendolo $R$ = \SI{85 \pm 1}{\centi\m} ciascuno (l'incertezza è 
maggiore della risoluzione del metro per tenere conto di errori nella valutazione del centro
di massa dei pendoli).
È importante notare che, per far sì che i pendoli oscillassero nello stesso piano
spaziale per tutta la durata dell'esperimento, i pendoli stessi fossero
liberi di muoversi lungo l'ansa creata dal filo di nylon appeso ai carrellini. 
A questo punto al pendolo di destra è stato collegato un breve tratto di spago 
per consentirne la manovra da una posizione che non interferisse con il tracking.
Di fronte a questa apparecchiatura, a una distanza di circa \SI{1.5}{\m}, è stato 
posizionato il treppede con sopra la macchina fotografica, per l'acquisizione
del video.
L'obiettivo della macchina fotografica è stato accuratamente posizionato, per evitare
offset prospettici in un unico verso, su un piano parallelo a quello di oscillazione dei
pendoli e la sua proiezione è stata fatta approssimativamente coincidere con il
centro della circonferenza passante per i due carrellini e i due pendoli a 
riposo.
L'apparato sperimentale completo è mostrato in \cref{setup_exp}

\begin{figure}[h!]
  \centering
  
  \caption{\textit{Schema dell'apparato sperimentale visto dalla fotocamera.}}
  \label{setup_exp}
\end{figure}

\subsection{Esecuzione dell'esperimento}

Una volta sistemati tutti gli elementi, sono stati acquisiti differenti video del fenomeno, avendo la cura di avere una condizione
iniziale statica, con i tutti gli elementi fermi rispetto al sistema di riferimento della stanza.
Questa ipotesi è stata realizzata 
inizialmente collegando, dopo aver fermato il pendolo di sinistra, 
con un lungo spago fatto circolare attorno all'apparato, il pendolo e il carrello di destra.
In questo modo si puntava ad eliminare l'errore dato dalla non coincidenza degli istanti
di rilascio dei due elementi, che sarebbero invece stati messi in moto nello stesso momento al 
taglio dello spago.
Questo sistema, però, è risultato inadatto in quanto lo spago, una volta tagliato, continuava a 
disturbare il movimento dell'apparecchio introducendo un nuovo attrito e 
distorcendo il fenomeno.
Si è provato quindi ad agire nel modo più semplice: fermando il pendolo di sinistra, trattenendo con una mano il carrellino di destra e con l'altra lo spago 
collegato al rispettivo pendolo.
Successivamente sono stati effettuati diversi rilasci, ed è 
stato scelto per l'analisi il video in cui il pendolo e il carrellino di sinistra venivano
sganciati approssimativamente nello stesso istante.
I video sono stati registrati con la risoluzione
di 1920 x 1080 pixel, ad un framerate di 25 FPS.
\label{sezione_realizz}

\subsection{Scrittura dei programmi per l'acquisizione e l'elaborazione dati}

Per quanto riguarda la scrittura dei programmi, si è scelto di utilizzare 
la libreria OpenCV, che sta per Open Computer Vision, una libreria open source 
utilizzabile in particolare nel linguaggio di programmazione C++, 
destinata all'analisi di immagini e video. 
In questo esperimento la libreria è stata utilizzata nel per tracciare il 
movimento nel tempo dei pendoli e dei carrellini, in maniera automatizzata.
E' stato utilizzato il C++ per la nota velocità in esecuzione rispetto a 
python. Il codice è listato in \cref{listatocpp}.
Il codice inizialmente acquisisce il percorso di memorizzazione del file video, per poi 
permettere all'utente di scegliere prima l'oggetto da tracciare
 e poi 
il numero progressivo dell'acquisizione.
In seguito viene chiesto all'utente di disegnare un rettangolo attorno
all'oggetto di interesse, partendo dal suo centro.
L'algoritmo di tracking, in questo caso KCF\footnote{https://arxiv.org/abs/1404.7584}, 
inizia poi a processare i vari frame, seguendo l'oggetto e scrivendo nel file
le coordinate in pixel del centro del rettangolo (l'origine è nell'angolo in alto a sinistra e gli assi 
sono diretti verso destra e verso il basso).
Vari momenti del processo appena descritto sono mostrati in \cref{photo_tracking}.

\begin{figure}[h!]
  \centering
\begin{minipage}{0.3\textwidth}
  \centering
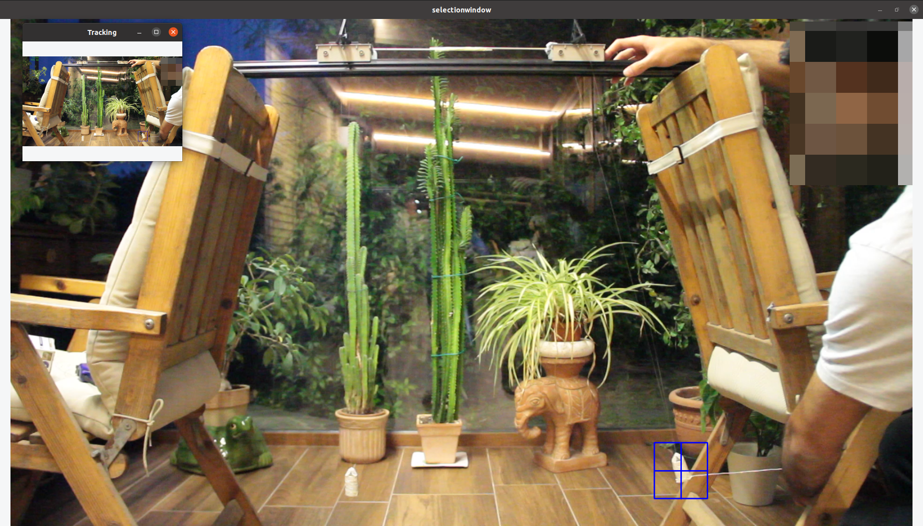
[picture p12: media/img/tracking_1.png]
  
\end{minipage}
\begin{minipage}{0.3\textwidth}
  \centering
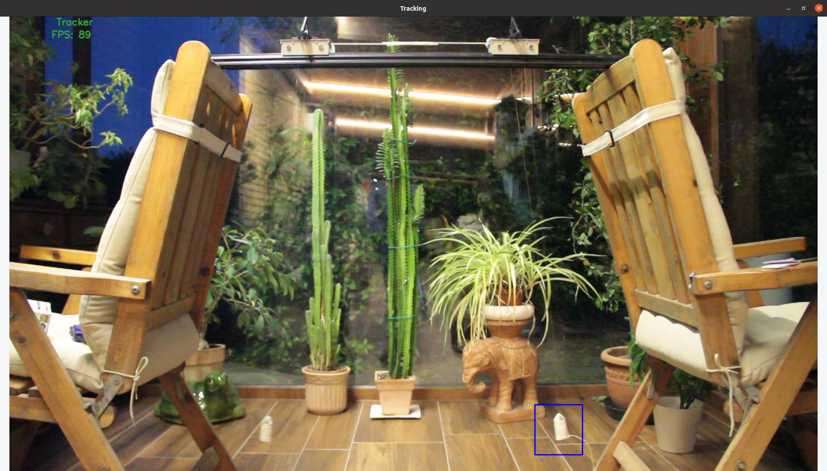
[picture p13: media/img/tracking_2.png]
  
\end{minipage}
\begin{minipage}{0.3\textwidth}
  \centering
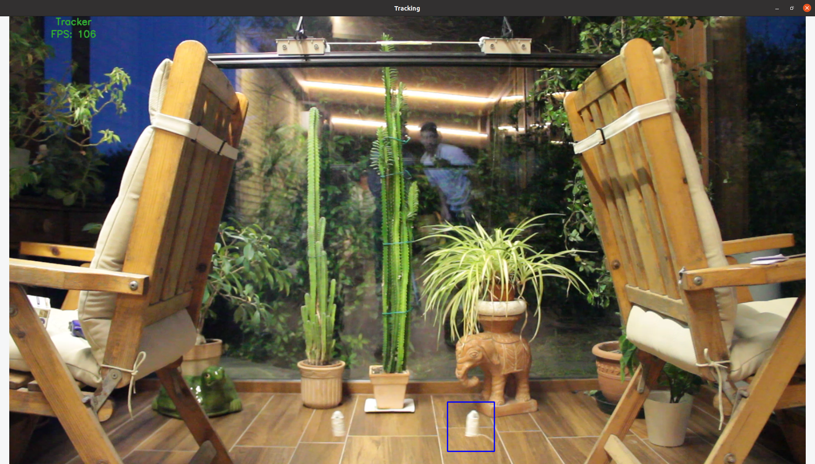
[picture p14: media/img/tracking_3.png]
  
\end{minipage}
\caption{\textit{Tre istanti del processo di tracking dell'oggetto.
Nell'immagine a sinistra si osserva il momento di selezione del pendolo, tracciando un rettangolo blu attorno 
allo stesso. Nelle altre due immagini sono mostrati due screenshot effettuati alla 
finestra di tracking, mentre l'algoritmo traccia l'oggetto desiderato, spostando il rettangolo blu.
Nell'immagine a sinistra si nota anche un istante del processo di rilascio descritto in \cref{sezione_realizz}}}
\label{photo_tracking}
\end{figure}
L'utente può e deve fermare l'acquisizione nel caso noti che il rettangolo
scompaia, accompagnato dal messaggio \textit{Tracking failure detected}, relativo al
caso in cui l'algoritmo non riesca a identificare la posizione dell'oggetto
in un determinato frame.

In seguito all'acquisizione di vari set dati, nel nostro caso 4 per ogni oggetto,
per cercare di limitare eventuali errori di posizione, è stata fatta 
una media tramite il programma in \cref{listatoavg}, stavolta scritto
in python per elasticità nella gestione dei dati in lettura e scrittura.
Sono così stati prodotti quattro files finali, uno per ogni elemento mobile.

Infine, nel listato in \cref{listatoplotter}, sono stati letti i quattro
files citati sopra, e sono stati poi ricavati con considerazioni
trigonometriche gli angoli indicati in \cref{pendolicorpolibero} come
$\theta_1$ e $\theta_2$. Sono quindi stati scelti degli intervalli 
temporali appropriati per effettuare i fit di funzioni del tipo presentato in 
\cref{equazionefinaleh,equazionefinaleq}, in particolare scartando 
i punti iniziali in cui l'apparecchio è fermo, oppure gli ultimi 
qualora il fenomeno da osservare non fosse più presente.

\section{Risultati e discussione}
Il grafico degli angoli $\theta_1$ e $\theta_2$ di \cref{pendolicorpolibero} 
al trascorrere del tempo, mediato sul 
numero di acquisizioni effettuate, è mostrato in
\cref{angles_full}, mentre è presente uno zoom sugli istanti iniziali in \cref{anlges_accurate},
e uno zoom sui massimi in \cref{angles_decrease}, in cui i punti sono stati collegati 
da linee continue.

\begin{figure}[h!]
  \centering
  
  \caption{\textit{Grafico completo dei due angoli $\theta_1$ e $\theta_2$ al trascorrere del tempo.} }
  \label{angles_full}
\end{figure}

\begin{figure}[h!]
  \centering
  
  \caption{\textit{Grafico dei due angoli $\theta_1$ e $\theta_2$ al trascorrere del tempo. Zoom sugli istanti iniziali.} }
  \label{anlges_accurate}
\end{figure}

\begin{figure}[h!]
  \centering
  
  \caption{\textit{Grafico dei due angoli $\theta_1$ e $\theta_2$
  al trascorrere del tempo, dettaglio delle creste. Si nota come la diminuzione delle ampiezze
  sia di intensità differente.} }
  \label{angles_decrease}
\end{figure}

In \cref{angles_full} si nota come, dopo un breve periodo iniziale di quiete, in cui il
pendolo $\mathbf{P}_1$ si trova in quiete, mentre il pendolo $\mathbf{P}_2$ descrive piccole
oscillazioni dell'ampiezza di circa 1°, che si è cercato di ridurre il più possibile manualmente,
il sistema viene lasciato libero di evolvere: il dettaglio è presente in \cref{anlges_accurate}.
Dopo un momento di transizione, in cui i pendoli e i carrellini descrivono il loro complicato moto,
circa dall'istante 4.6 all'istante 8.5, il sistema mantiene il suo moto nella condizione di
oscillazioni in controfase, quindi con i carrellini necessariamente fermi, per la conservazione
della quantità di moto iniziale, nulla. I pendoli quindi sono stati sincronizzati.
È facile osservare come $\mathbf{P}_1$, che parte da fermo, non ha delle oscillazioni
centrate sugli 0°, errore probabilmente dovuto al tracciamento effettuato in prospettiva.
Si tratta di un errore che, seppur minimo, è sistematico e si continua a manifestare in tutto il moto, 
con la traslazione verso l'alto di tutto il grafico di circa 1°.
Nella \cref{angles_decrease}, dove i punti sono stati collegati da una linea continua nell'
intento di essere più chiari, si nota come sia presente un'evidente differenza nelle oscillazioni 
dei due pendoli: l'ampiezza del pendolo $\mathbf{P}_2$ risulta decrescere più rapidamente rispetto
all'altra: un probabile effetto di un maggiore attrito influente sul pendolo stesso, ad esempio
a livello del perno. Non si tratta infatti di un offset prospettico in quanto dalla \cref{angles_full}
è evidente come la diminuzione dell'ampiezza sia presente simmetricamente, anche a livello dei
minimi di oscillazione.

Possono quindi essere costruite e analizzate le variabili $h$ e $q$, definite nel sistema \labelcref{definizionehq}
e mostrate al variare del tempo nelle \cref{fit_h,fit_q}.
In queste due figure sono anche presenti i due fit delle equazioni teoriche che dovrebbero regolare,
secondo le ipotesi indicate in \cref{sezioneattrito}, il moto delle due variabili, ossia le \cref{equazionefinaleh,equazionefinaleq}.
In basso nelle figure sono mostrati anche i residui, ossia la differenza
, calcolata punto per punto, tra i valori del fit e quelli dei punti acquisiti.
\begin{figure}[h!]
  \centering
  
  \caption{\textit{Modello del sistema costruito con indicate
   le grandezze rilevanti. Le lettere maiuscole in grassetto indicano dei punti, quelle in corsivo delle 
   costanti; le minuscole invece indicano le variabili. In basso il grafico dei residui.} }
  \label{fit_h}
\end{figure}

\begin{figure}[h!]
  \centering
  
  \caption{\textit{Modello del sistema costruito con indicate
   le grandezze rilevanti. Le lettere maiuscole in grassetto indicano dei punti, quelle in corsivo delle 
   costanti; le minuscole invece indicano le variabili. In basso il grafico dei residui.} }
  \label{fit_q}
\end{figure}

È evidente come non siano presenti pattern che possano dare l'idea di un qualche effetto
sistematico che si potrebbe star trascurando; invece si può ragionevolmente ipotizzare la sola 
presenza di errori casuali, anche dovuti all'imprecisione del metodo di acquisizione, come si nota
dalla distribuzione più o meno casuale dei punti.

Alcuni dubbi sorgono osservando la \cref{fit_h}
, in particolare gli istanti successivi agli \SI{8}{\s}: sembra permanga un'oscillazione
residua, che si traduce in una non esatta sincronia nel movimento dei pendoli; 
praticamente quando un pendolo si trova in una posizione l'altro non si trova nella 
posizione simmetrica, ma leggermente spostato da questa.
L'origine di questo fenomeno non sembra essere dovuto al differente
attrito presente sui due perni, mostrato in \cref{angles_decrease}, in quanto
l'oscillazione residua si mantiene anche al diminuire dell'ampiezza delle
oscillazioni del pendolo più smorzato; il fenomeno potrebbe invece essere 
provocato dalla minima differenza di lunghezza 
dei pendoli, o semplicemente dalla predominanza di fenomeni di attrito statico 
su quelli dinamici.
Infatti, quando i carrellini si fermano, circa agli \SI{8.5}{\s}, interviene non
più l'attrito dinamico ma quello statico, che è caratterizzato da una maggiore intensità
è quindi immune a minime deviazioni che si potrebbero manifestare nella asincronia del moto.

Per quanto riguarda gli errori sulle acquisizioni di posizione, questi non sono stati
stimati a causa della mancanza di informazioni sulla confidenza dell'algoritmo di tracking.

I parametri delle funzioni $h(t)$ \labelcref{equazionefinaleh} e $q(t)$ \labelcref{equazionefinaleq}, stimati dal fit, sono elencati rispettivamente 
nelle \cref{parametrih,parametriq}.
In tabella è indicata anche la somma degli scarti quadratici tra il fit e i punti, il
$\chi^2_h$, indicatore numerico della bontà del fit.
\begin{table}[h!]
  \centering
\begin{minipage}{0.45\linewidth}
  \centering
  \begin{tabular}{cc}
      \toprule
      \multicolumn{2}{c}{Parametri $h(t)$} \\ 
      \midrule
      $A_h$     & \ang{92 \pm 5} \\
      $\gamma_h$& \SI{0.77 \pm 0.02}{\hertz} \\
      $\tilde{\omega}_h$& \SI{5.17 \pm 0.01}{\hertz}\\
      $\beta_h$   &  \SI{1.63 \pm 0.06}{}  \\
      $\chi^2_h$   &  \SI{29.6}{}  \\
      \midrule
    \end{tabular}
  \caption{\textit{Parametri ottenuti dal fit della funzione $h(t)$ \labelcref{equazionefinaleh}.}}
  \label{parametrih}
\end{minipage}
\begin{minipage}{0.45\linewidth}
  \centering
    \begin{tabular}{cc}
        \toprule
        \multicolumn{2}{c}{Parametri $q(t)$} \\ 
        \midrule
        $A_q$     & \ang{14.85 \pm 0.01} \\
        $\gamma_q$& \SI{0.00631 \pm 0.00006}{\hertz} \\
        $\tilde{\omega}_q$& \SI{3.40231 \pm 0.00003}{\hertz}\\
        $\beta_q$   &  \SI{0.275 \pm 0.001}{}  \\
        $\chi^2_q$   &  \SI{26.1}{}  \\
        \midrule
      \end{tabular}
    \caption{\textit{Parametri ottenuti dal fit della funzione $q(t)$ \labelcref{equazionefinaleq}.}}
    \label{parametriq}
\end{minipage}
\end{table}
In realtà il fit è stato effettuato anche con un ulteriore grado di libertà, aggiungendo
un parametro responsabile della traslazione dei grafici delle funzioni rispetto 
all'asse $y$; questo non è stato però riportato in quanto per il miglior fit
tale parametro restava nullo.

Calcolando poi i valori delle frequenze $\omega$, definite in \cref{sezionesenzaattrito},
e notando che per i valori di $\gamma$ ottenuti dai fit 
$\omega_i^2 \gg \left( \frac{\gamma_i}{2} \right)^2$, e conseguentemente in
\cref{equation:omegadef} si ha $ \tilde{\omega}_i \approx \omega_i$ per $i=h,q$,
si ottiene:
\begin{align*}
\tilde{\omega}_h \approx \omega_h = \SI{5.62 \pm 0.04}{\hertz} \, , \\
\tilde{\omega}_q \approx \omega_q = \SI{3.40 \pm 0.02}{\hertz} \, ,
\end{align*}
dati che risultano essere in accordo quasi soddisfacente con i risultati del fit delle \cref{parametrih,parametriq}.
È presente una maggiore discordanza per quanto riguarda $\omega_h$, dell'8\%, dovuta 
alle varie sorgenti di errore citate in precedenza ma anche al minor numero di punti disponibili
per il fit.

Notiamo infine che la stima dei coefficienti di attrito data dal fit è in accordo 
con l'idea intuitiva legata alla caratteristica del modo di oscillazione in cui il carrello 
è fermo, ossia alla minor dissipazione di energia rispetto a quello in cui il carrello oscilla in opposizione di 
fase rispetto ai pendoli; ciò è dovuto soprattutto al maggiore attrito generato
durante lo scorrimento sulla rotaia che si somma al normale attrito generato sul perno 
dalle oscillazioni dei pendoli. Questa sorgente di attrito è circa di 2 ordini di grandezza superiore 
rispetto all'altra.
\section{Conclusioni}
In conclusione, è stata osservata con successo la sincronizzazione di due pendoli, ossia la 
 diminuzione dell'ampiezza a zero di un modo normale di oscillazione del sistema, fatto dovuto a differenti
tassi di dissipazione di energia nei due modi appena citati. I due coefficienti $\gamma_h$ 
e $\gamma_q$ sono stati stimati essere pari rispettivamente a \SI{0.77 \pm 0.02}{\hertz} e 
\SI{0.00631 \pm 0.00006}{\hertz}.

\section{Appendice}
Nei seguenti listati sono presenti i file con i quali sono stati estratti 
e visualizzati i dati dell'esperimento.
\subsection{Listato del programma di tracking (C++)}
\lstinputlisting[language=C++]{../c++/tracking.cpp}
\label{listatocpp}
\subsection{Listato del programma di elaborazione dei dati (python)}
\lstinputlisting[language=Python]{../python/avg.py}
\label{listatoavg}
\subsection{Listato del programma di fit e visualizzazione dati (python)}
\lstinputlisting[language=Python]{../python/plotter.py}
\label{listatoplotter}

\end{document}

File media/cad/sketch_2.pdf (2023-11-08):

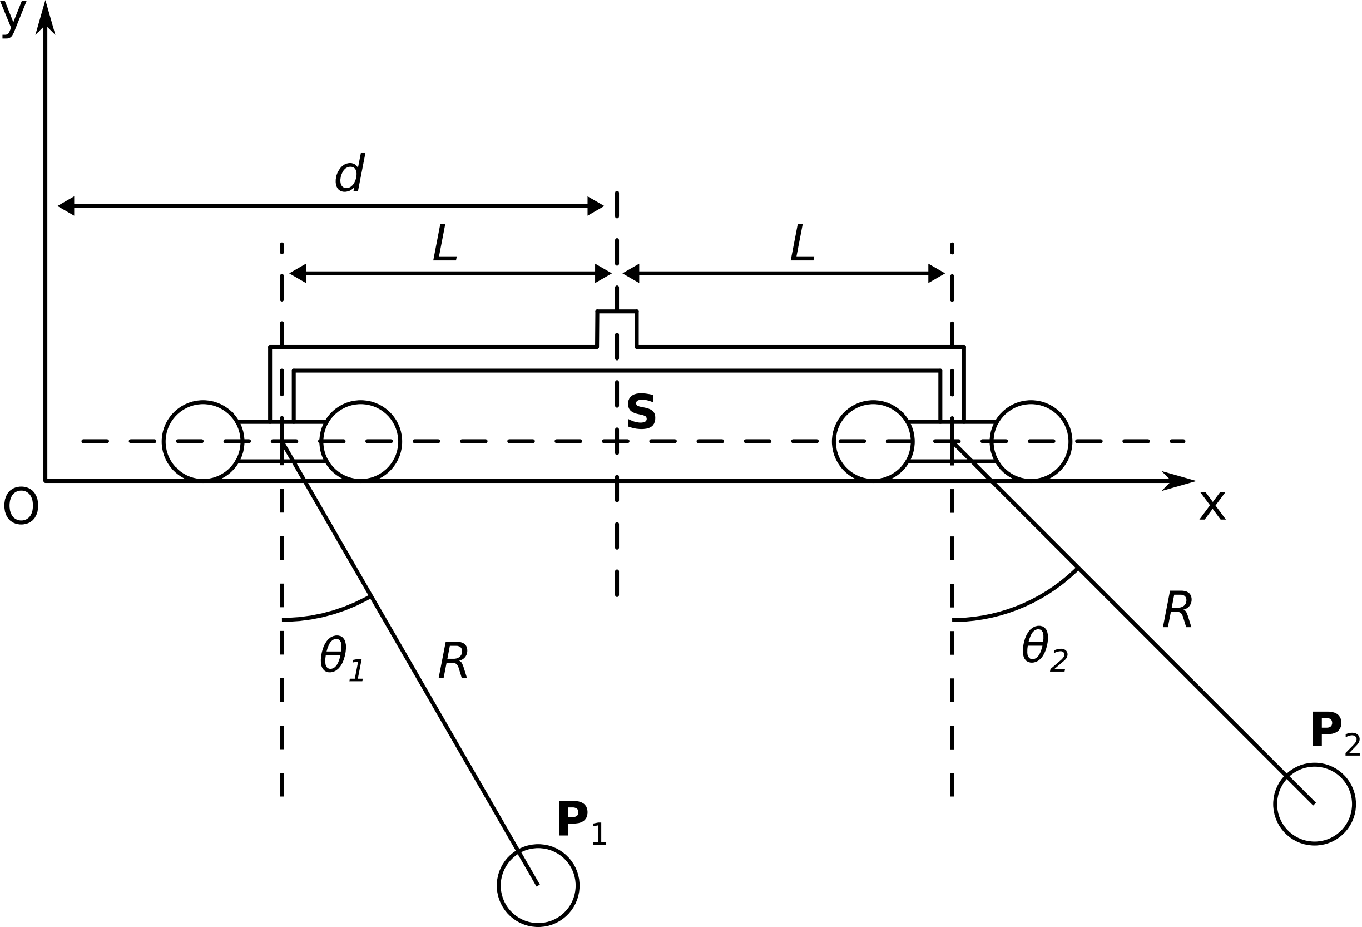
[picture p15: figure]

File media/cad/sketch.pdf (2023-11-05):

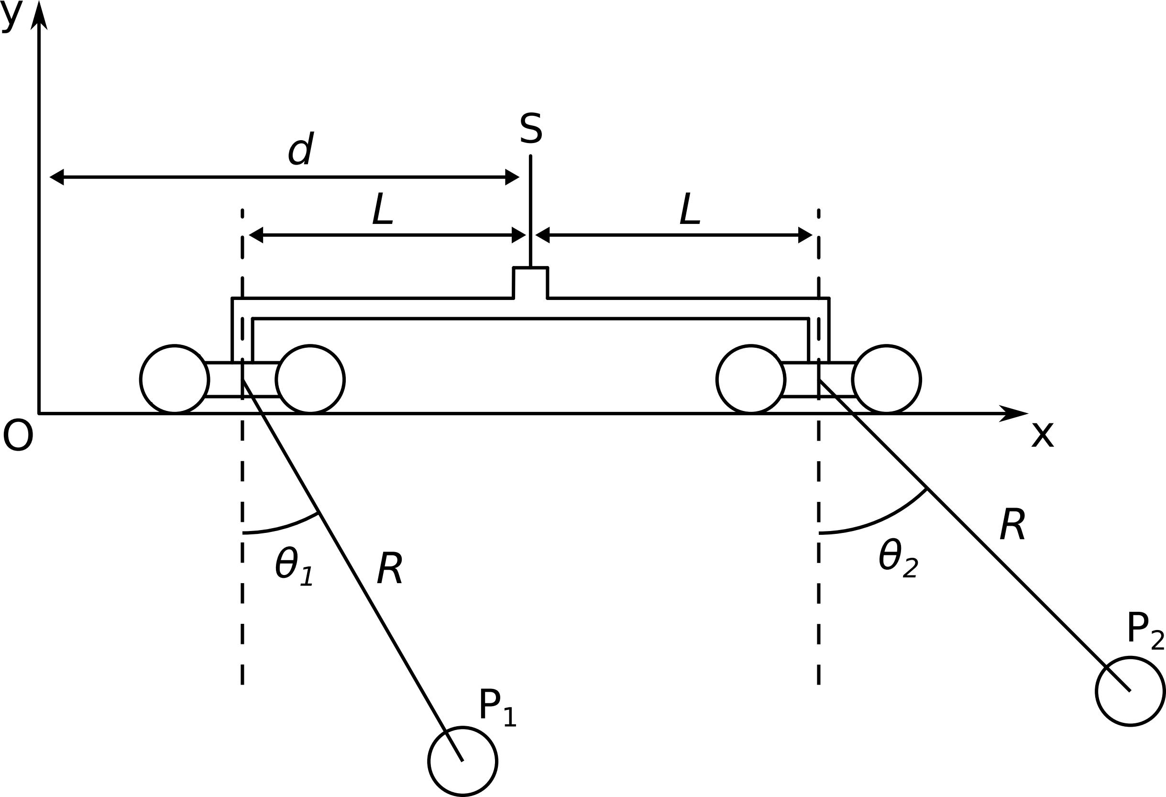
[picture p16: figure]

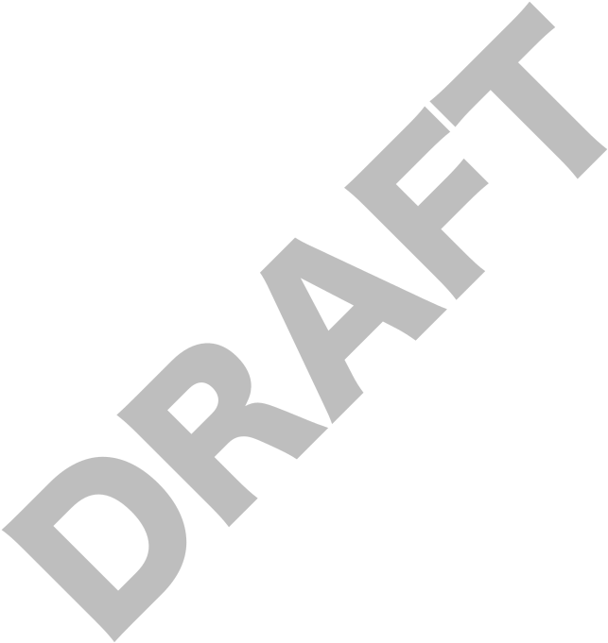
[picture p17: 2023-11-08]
media/img/draft_watermark.png

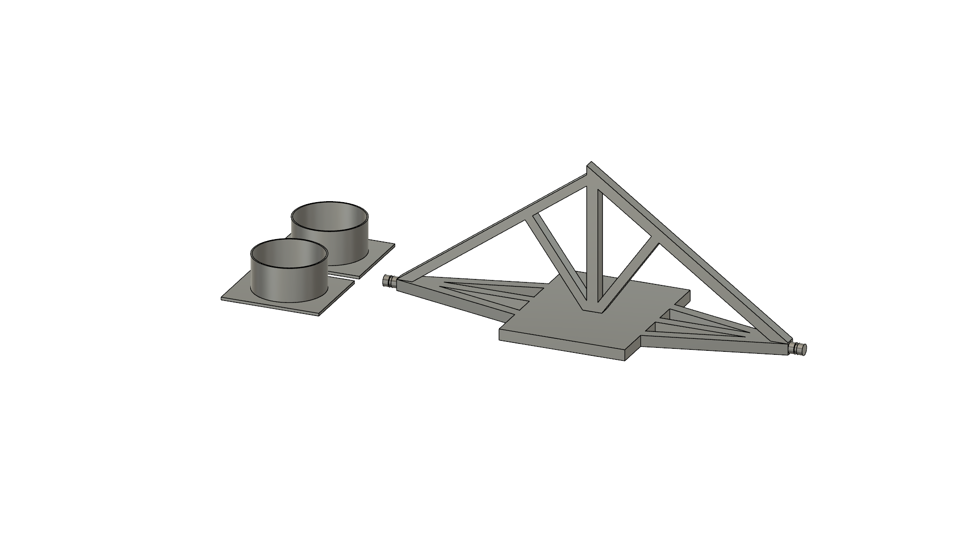
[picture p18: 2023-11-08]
media/img/fusion_project.png

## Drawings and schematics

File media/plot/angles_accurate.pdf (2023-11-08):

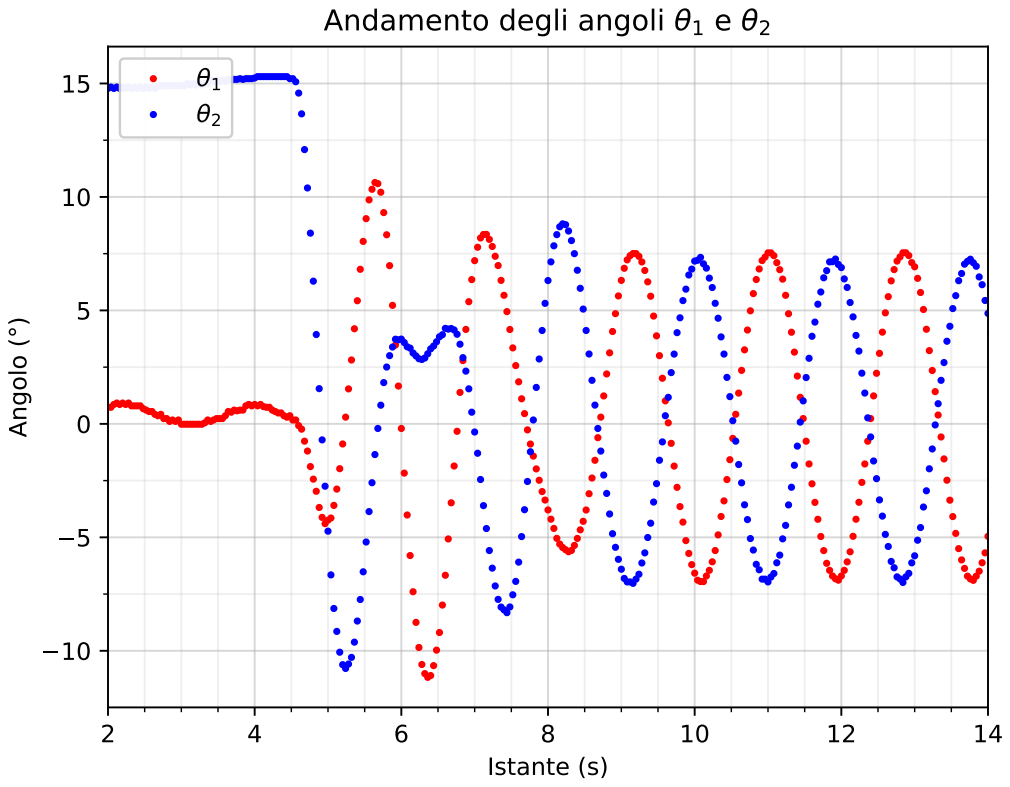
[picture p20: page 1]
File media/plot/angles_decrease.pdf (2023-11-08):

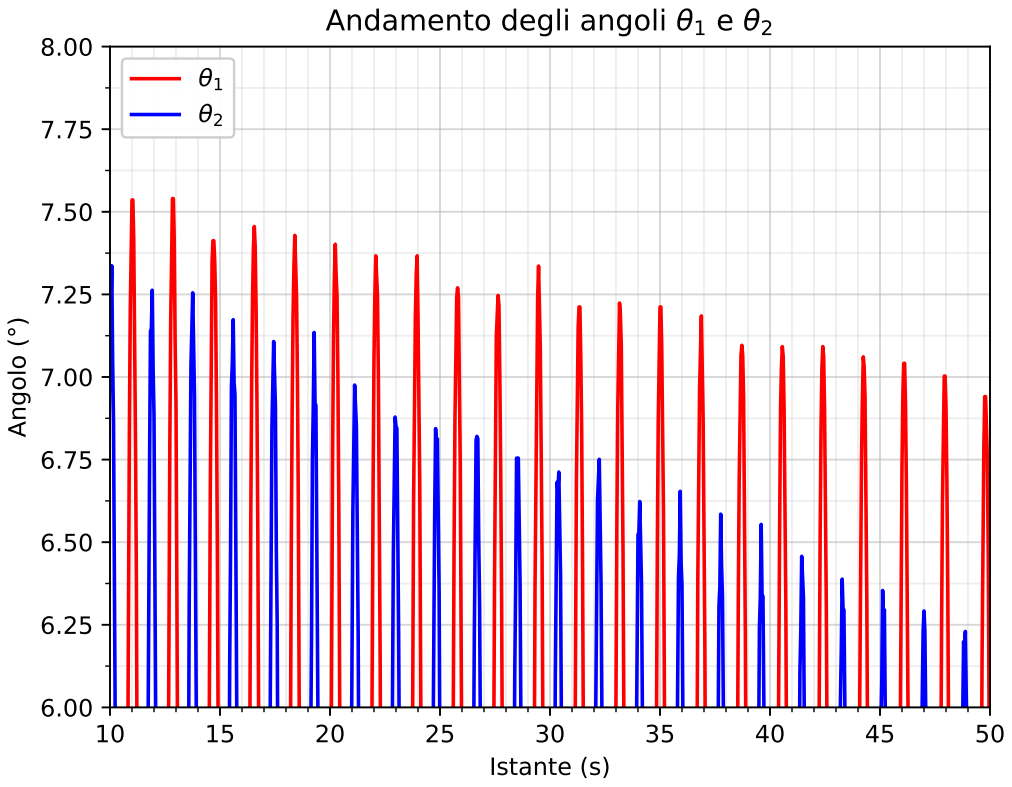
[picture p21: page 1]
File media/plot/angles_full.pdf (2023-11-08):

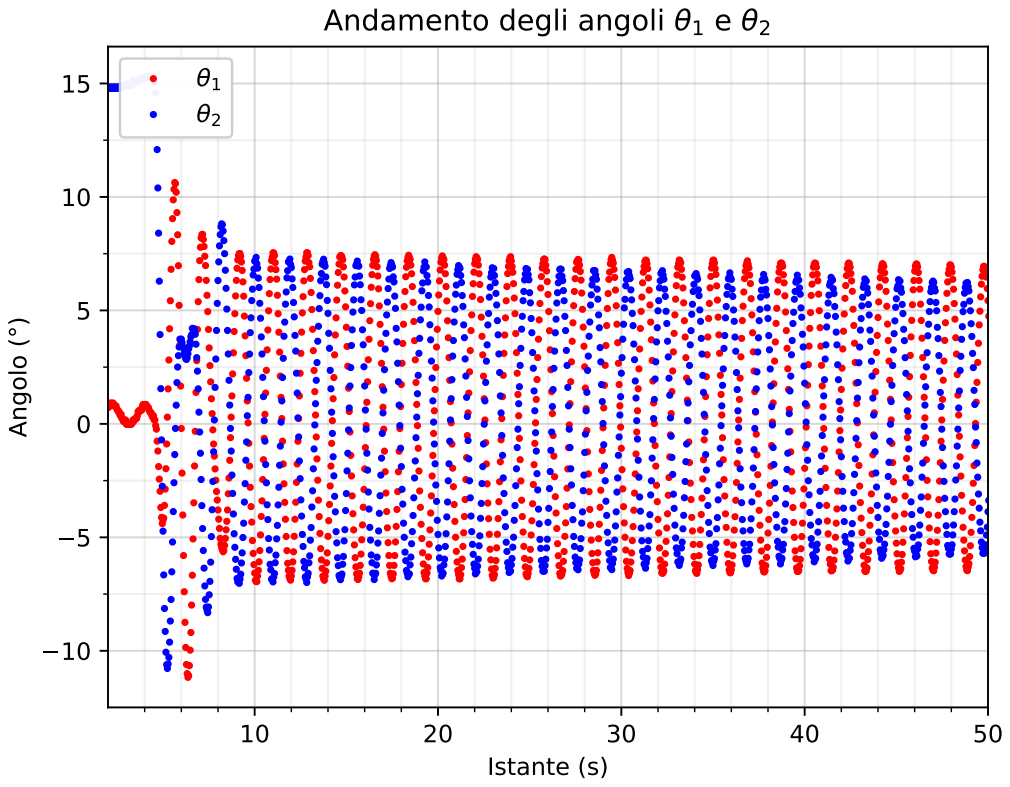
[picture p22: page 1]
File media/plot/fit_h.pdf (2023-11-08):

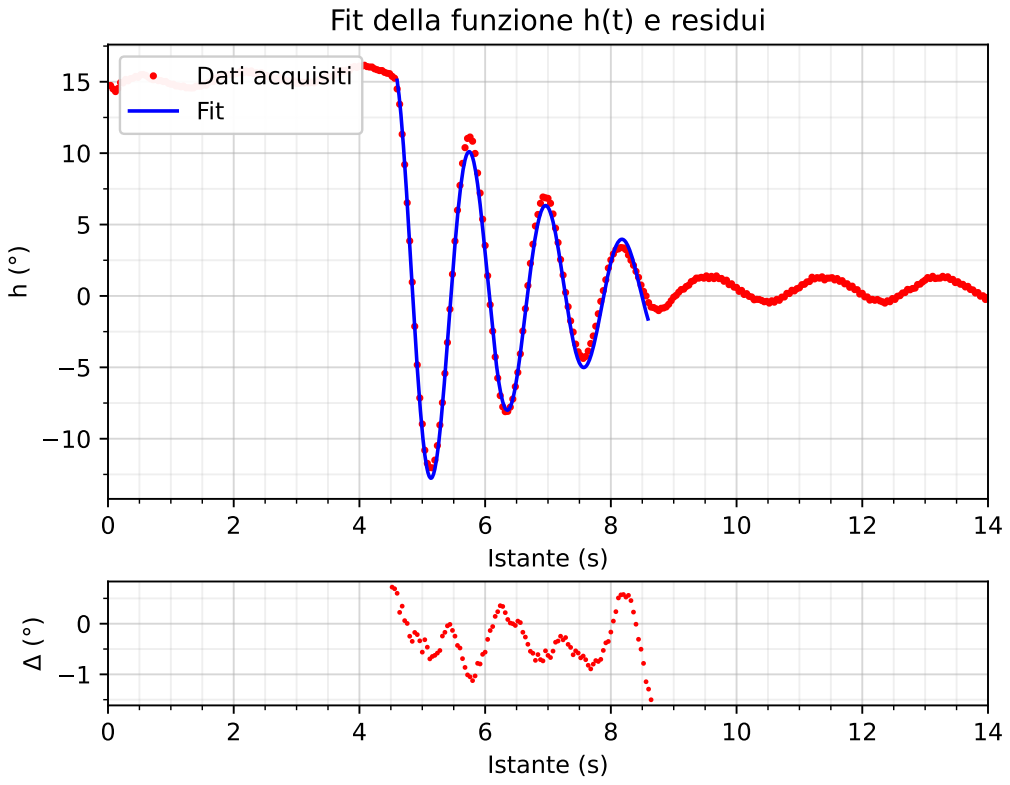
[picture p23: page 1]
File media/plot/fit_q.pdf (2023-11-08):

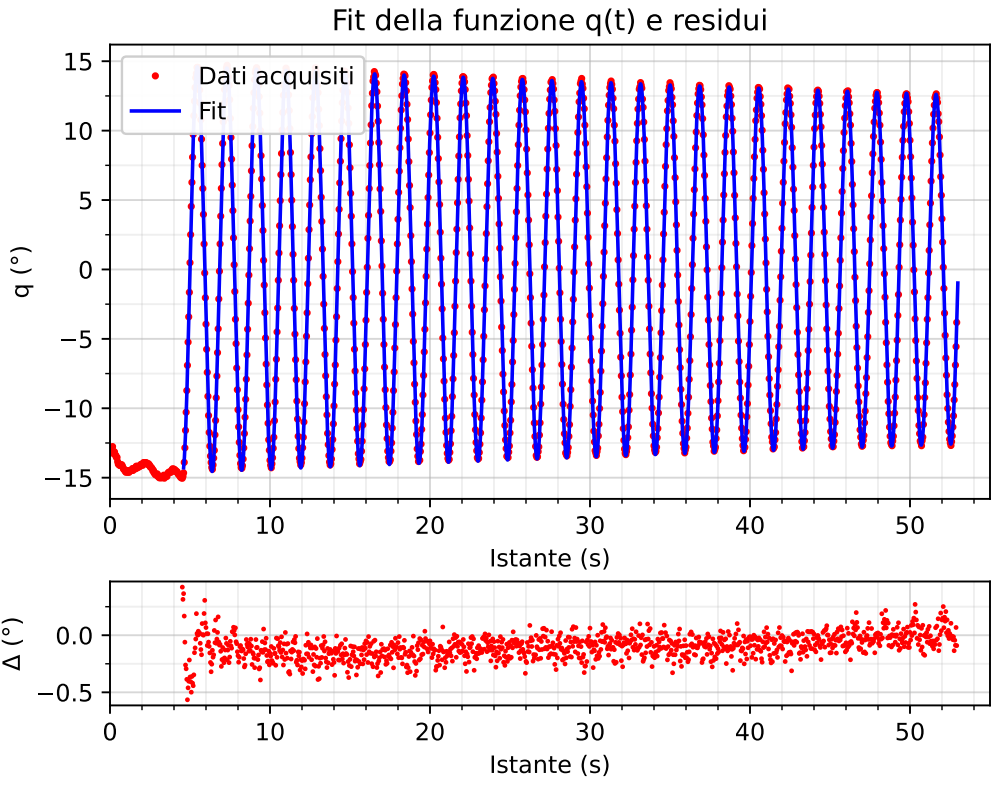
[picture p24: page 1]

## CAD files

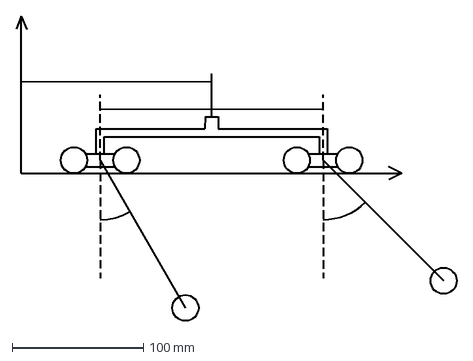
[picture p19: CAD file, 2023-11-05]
media/cad/prova.dxf
335.9 x 232.6 mm
